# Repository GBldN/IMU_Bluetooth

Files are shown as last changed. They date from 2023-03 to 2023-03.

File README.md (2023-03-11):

# IMU_Bluetooth
<p align="center">
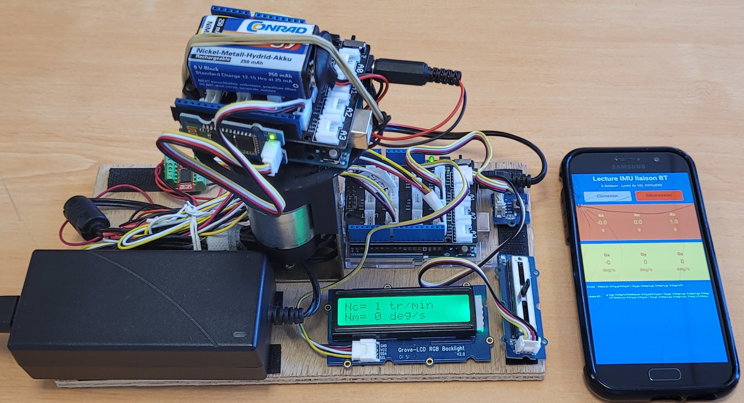
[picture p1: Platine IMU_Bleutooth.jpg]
Moteur à l'arret

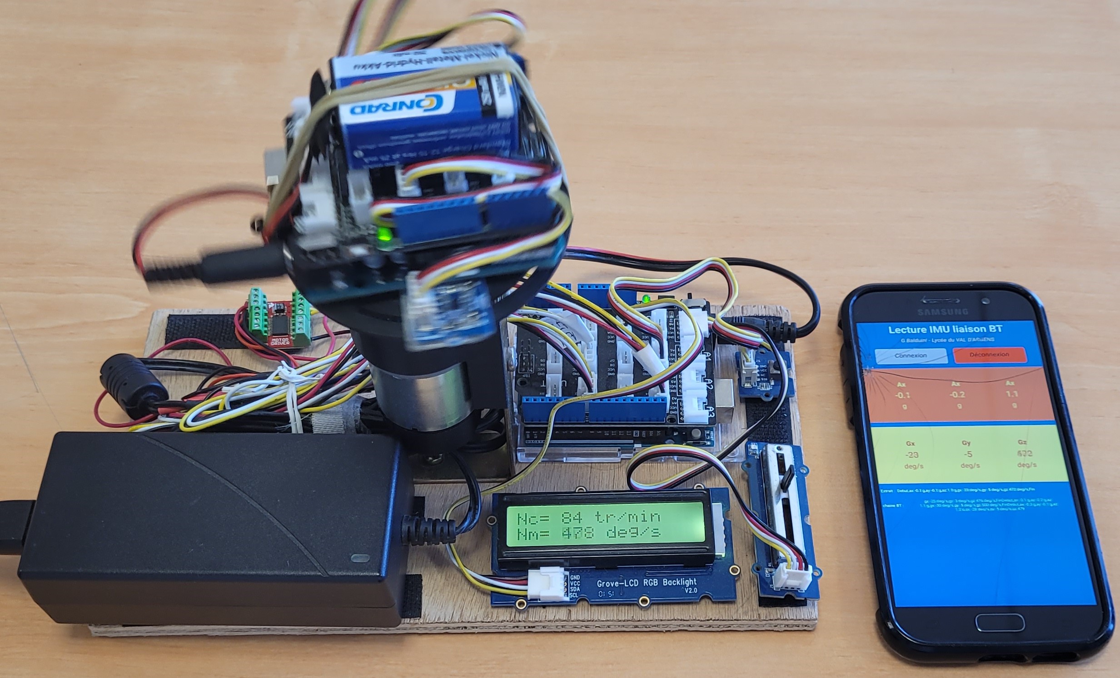
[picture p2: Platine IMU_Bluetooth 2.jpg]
Moteur en rotation
 
</p>

## Présentation

Platine expérimentale pour afficher, en temps réel, les données lues par une centrale inertielle incluant un accéléromètre et un gyromètre.
Il est possible de piloter la fréquence avec un potentiomètre linéaire.
L'écran LCD permet d'afficher la fréquence de consigne (en tr/min) et la mesure de la vitesse angulaire en °/s.
Les données de la centrale sont envoyées en Bluetooth vers un smartphone et une application spécifique.

Une vidéo du programme en situation est disponible  [youtu.be/u4rxh-nPM8k](https://youtu.be/_Ql979rKE8E)

## Matériel utilisé
### Centrale inertielle :
- Un Arduino UNO
- Une centrale inertielle Grove_IMU_6 DOF : [wiki.seeedstudio.com/Grove-6-Axis_AccelerometerAndGyroscope](https://wiki.seeedstudio.com/Grove-6-Axis_AccelerometerAndGyroscope/) 
- Un module Bluetooth Grove - Serial Bluetooth v3.0 [wiki.seeedstudio.com/Grove-Serial_Bluetooth_v3.0](https://wiki.seeedstudio.com/Grove-Serial_Bluetooth_v3.0/)
- Une pile 9V pour l'alimentation

### Banc moteur
- Un Arduino UNO
- Un écran LCD RGB BLACKLIGHT : [wiki.seeedstudio.com/Grove-LCD_RGB_Backlight](https://wiki.seeedstudio.com/Grove-LCD_RGB_Backlight/)
- Un potentiomètre linéaire Grove Slide Potentiometer : [wiki.seeedstudio.com/Grove-Slide_Potentiometer](https://wiki.seeedstudio.com/Grove-Slide_Potentiometer/)
- Un Driver moteur Sparkfun TB6612FNG : [sparkfun.com/tutorials/tb6612fng-hookup-guide](https://learn.sparkfun.com/tutorials/tb6612fng-hookup-guide?_ga=2.155362748.600943259.1678452372-1239022160.1678452372)
- Un moto réducteur POLOLU #4753 avec une réduction de 50:1 et 64CPR (rise and fall) : [pololu.com/product/4753](https://www.pololu.com/product/4753)
- Une équerre de renfort Zingué 100x100x22mm
- Une interface de fixation du motoréducteur sur l'équerre, imprimée en 3D (voir fichier stl)
- Un plateau à fixer sur la sortie du motoréducteur imprimé en 3D (voir fichier stl)
- Une alimentation CC 12V 3A ou plus

### Application Android
L'application permet d'afficher en temps réel :
- les 3 valeurs Ax, Ay et Az de l'accéléromètre
- Les 3 valeurs Gx, Gy et Gz du gyromètre

L'Arduino envoie, par la liaison bluetooth, une chaine de caractères :  
"Debut,ax:±##.##;g,ay:±##.##;g,ay:±##.##;g,gx:±####;deg/s,gy:±####;deg/s,gz:±####;deg/s,Fin  "  
Dont les ### sont les valeurs de chaque composante.

L'application a été développé avec APP INVENTOR :  [appinventor.mit.edu/](https://gallery.appinventor.mit.edu/?galleryid=7bed003b-4152-40f3-b9e8-77ac0583e04f)
Le fichier apk est fourni dans les fichiers

### Explications :
Le principe est le suivant :
- Le µC de la centrale envoie en permanence les 6 composantes d’accélérations et de vitesses angulaires en temps réel par l’intermédiaire du Bluetooth
- Le smartphone affiche les 6 valeurs.
- On peut contrôler « précisément » la fréquence de rotation du motoréducteur et lire sur la platine la valeur « réelle » en °/S
- Il est donc possible de vérifier les valeurs mesurées par le gyromètre en °/S et éventuellement celle de l’accéléromètre (accélération centripète) a= ω²∙ Rayon

Pour tout renseignement complémentaire [gael.balduini@gmail.com](mailto:gael.balduini@gmail.com)

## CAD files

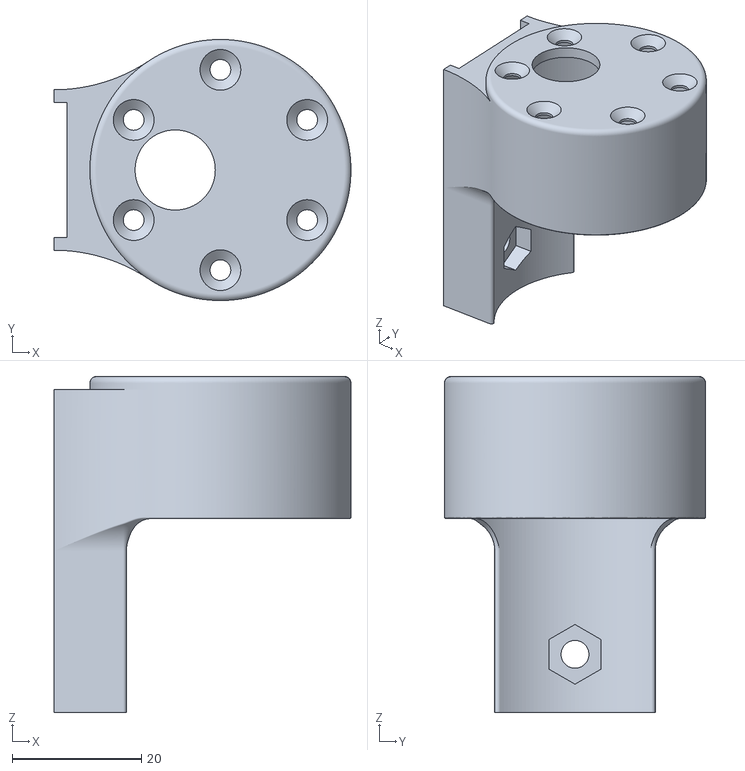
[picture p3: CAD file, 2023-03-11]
Support Moteur Pololu 37D.STL
46.0 x 40.4 x 52.0

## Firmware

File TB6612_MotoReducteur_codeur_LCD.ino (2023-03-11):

/* ################# PROGRAMME DE PILOTAGE D'UN MOTOREDUCTEUR AVEC LE DRIVER TB6612FNG  #################
 * Programme pour piloter en vitesse un moto réducteur à partir d'un signal PWM et mesurer la fréquence de rotation avec son codeur.
 * 
 * Le mini driver moteur utilisé est un Sparkfun TB6612FNG https://www.sparkfun.com/products/14451 qui permet de controler 2 moteurs CC jusqu'à 1,2A par canal
 * Le moteur utilisé est un POLOLU #4753 avec une réduction de 50:1 et 64CPR (rise and fall)  https://www.pololu.com/product/4753
 * Son codeur doit être connecté aux 2 entrées d'interruption INT0 sur D2 et INT1 sur D3.
 * Mais il est possible d'adapter le programme à n'importe quel moteur et codeur.
 * 
 * Ce programme permet :
 *  - De controler la variation de vitesse ainsi que le sens de rotation par un potentiomètre (arrêt en position médiane) 
 *  - De Mesurer les 2 impulsions du codeur grâce à la lecture des interruptions
 *  - De calculer la fréquence de rotation DE LA SORTIE DU REDUCTEUR en tenant compte CPR (nombre d'implusions par tour) ainsi que le rapport de réduction du réducteur
 *  - D'afficher la valeur de Fréquence de consigne et de fréquence mesuré sur un écran LCD
 *  
 * Le calcul à intervalle régulier est géré par le TIMER2 controlé par les registres
 *  
 * Un exemple d'application est disponible sur le github https://github.com/GBldN/IMU_Bluetooth
 * 
 * Une vidéo du programme en situation est disponible sur youtube https://youtu.be/u4rxh-nPM8k
 *  
 * version=1.0
 * author=gael.balduini@gmail.com
 * licence=CC-by-nc-sa
 * maintainer=Arduino <info@arduino.cc>
 * category=Data Processing
 */

/* ##### PARAMETRES POUR PERSONNALISER LE MATERIEL ##### */
  #define f_ech             50                //Choix d'une fréquence en Hz pour le calcul à intervalle régulier
  #define prediviseur       64                //Prédiviseur du timer 2 pour un réglage de l'interruption à 976,5625 Hz
  #define TCNT_init         6                 //Choix d'une valeur de départ du comptage pour régler une fréquence de 1000 Hz
  #define f_timer()         (16000000 / prediviseur / ( 256 - TCNT_init))   //Calcul de la fréquence d'interruption
  
  #define CPRtick           64                //Nombre de ticks par tour du codeur (fonction du codeur utilisé)
  #define reduction         50                //Rapport de réduction du réducteur entre le codeur et l'arbre de sortie
  #define N_max             220               //Fréquence de rotation maxi de l'arbre de sortie ( ± en tr/min)
  #define Offset            10                 //Offset +/- pour l'arrêt du piltage de l'arbre de sortie (en tr/min) nécessaire pour la stabilité à l'arrêt
 
/* ##### DEFINITION DES CONNEXIONS ##### */
  #define An0_Pin           A0                //Port de connexion de l'entrée du CAN An0
  #define Bp1Pin            8                 //Port de connexion de l'entrée du bouton poussoir de calibrage (en option)

  #define MotSTBYPin        4                 //Port de connexion du signal STANDBY du driver de puissance
  #define MotPWMAPin        5                 //Port de connexion du signal PWMA du driver de puissance
  #define MotAIN1Pin        6                 //Port de connexion du signal AIN1 du driver de puissance
  #define MotAIN2Pin        7                 //Port de connexion du signal BIN1 du driver de puissance



/* ##### DEFINITION DES BIBLIOTHEQUES ET DES VARIABLES ##### */
/* -- Intégrations des bibiothèques -- */
 #include <Wire.h>                            //Intégration de la bibliothèque "wire" pour la gestion de l'I2C
 #include "rgb_lcd.h"                         //Intégration de la biblitothèque "rgb_lcd" pour la commande de l'écran GROVE I2C
 rgb_lcd lcd;                                 //Création de la fonction nommée ici "lcd"

/* -- Définition des variables pour l'état TOR ou les valeurs numériques des entrées -- */
  uint16_t           An0            = 0;      //Variable pour la position du potentiomètre de réglage de la consigne de 0 à 1024 (CAN 10 bits)
  bool               etat_BP        = false;  //Variable pour connaitre l'état du bouton poussoir
  volatile int32_t   tics            = 0;      //Variable pour le nombre de tics du capteur
  int32_t            tics_precedent  = 0;      //Variable pour le calcul de la fréquence
  uint32_t           t0             = 0 ;     //Variable pour le calcul du temps

  /* -- Définition des variables pour le pilotage -- */
  float              N_consigne     = 0;      //Variable pour la consigne de fréquence de rotation en tr/min
  float              N_mesure       = 0;      //Variable pour la fréquence réelle mesurée en tr/min
  float              erreur         = 0;      //Variable pour la mémorisation de la vitesse
  int16_t            MLI_mot        = 0;      //Variable pour le réglage du rapport cyclique du moteur

/* -- Déclaration des fonctions utiles au programme -- */
  uint8_t            compteur       = 0;      //Compteur pour le régalge de l'opération à lancer à la fréquence choisie
  uint8_t            CouleurR       = 0;      //Variable pour la gestion de la couleur Rouge de l'écran LCD
  uint8_t            CouleurV       = 255;    //Variable pour la gestion de la couleur Verte de l'écran LCD
  uint8_t            CouleurB       = 0;      //Variable pour la gestion de la couleur Bleu de l'écran LCD


  
/**************************************************************
      ROUTINE D'INITIALISATION  (exécutée une seule fois)
 **************************************************************/
void setup()
{
/* -- Configuration des broches en ENTREE ou SORTIE -- */
  pinMode(An0_Pin,          INPUT);
  pinMode(Bp1Pin,           INPUT);
  pinMode(MotAIN1Pin,       OUTPUT);
  pinMode(MotAIN2Pin,       OUTPUT);
  pinMode(MotPWMAPin,       OUTPUT);
  pinMode(MotSTBYPin,       OUTPUT);

  pinMode(2,       INPUT_PULLUP);
  pinMode(3,       INPUT_PULLUP);

  TWBR = ((F_CPU / 400000L) - 16) / 2;          //Réglage de la fréquence de fonctionnement du bus I2C à 400kHz
  setup_timer2();                               //Appel de la routine de configuration du timer 2
  


/* -- configuration des fonctions spéciales nécessaires au programme */
  Serial.begin(115200);                       //Initialisation de la bibliothèque Moniteur série
  lcd.begin(16, 2);                             //Démarrage et configuration de la fonction LCD pour un écran 2 lignes 16 caractères
  lcd.clear();                                  //Effacement de l'écran
  lcd.setRGB(0, 255, 0);                        //Réglage de la couleur de l'écran en VERT
  lcd.setCursor(0, 0);                          //Positionnement du curseur (caractère,ligne)
  lcd.print("PILOTAGE VITESSE");                //Ecriture du titre du programme sur le LCD
  lcd.setCursor(0, 1);
  lcd.print(" CODEUR ROTATION");                //Explication du role du bouton d'initialisation
  delay(2000);                                  //Pause pour l'affichage du nom du programme
  lcd.clear();

  attachInterrupt(digitalPinToInterrupt(2), Comptage, CHANGE);  //Création de l'interruption sur la broche INT0 : D2
  attachInterrupt(digitalPinToInterrupt(3), Comptage2,CHANGE);  //Création de l'interruption sur la broche INT1 : D3                                
  
  digitalWrite(MotSTBYPin,HIGH);                //mise à 1 du signal STANDBY du driver pour son activation
  t0 = millis();
}

/**************************************************************
           BOUCLE PRINCIPALE (exécutée en permanence)
 **************************************************************/
void loop()
{ 
/* -- Lecture des valeurs de entrées -- */
  An0  = analogRead(An0_Pin);                   //Lecture de la valeur du CAN de l'entrée A0
  N_consigne = map(An0,0,1023,-N_max,N_max);    //Définition de la valeur ± de fréquence de consigne en tr/min
 
/* -- Arret du moteur en cas d'appui sur le bouton poussoir -- */
 /* if ( digitalRead(Bp1Pin) == HIGH && etat_BP == false )
  {
    digitalWrite(MotSTBYPin,LOW);                //mise à 0 du signal STANDBY du driver pour son activation
    etat_BP = true;
  }
  
  if ( digitalRead(Bp1Pin) == LOW )
  {
    digitalWrite(MotSTBYPin,HIGH);                //mise à 1 du signal STANDBY du driver pour son activation
    etat_BP = false;
  }
*/
/* -- Affichage sur le moniteur série -- */
  Serial.print("N_consigne= " + String(N_consigne) + " tr/min ; N_mesure = " + String(N_mesure) + " tr/min"  );
  Serial.print(" | Pilotage moteur : " + String(MLI_mot));  Serial.print(" | tics = " + String(tics));
  Serial.println();

 PILOTAGE_MOTEUR();                             //Appel de la routine de pilotage du moteur

/* -- Gestion de la couleur de l'écran en fonction de la valeur du CAN  -- */
  
/* -- Affichage des valeurs sur l'écran tous les 200 ms-- */
  if ( ( millis() - t0 ) > 400 )
  {
    if ( abs(N_mesure) <= Offset )                      //Si la valeur du CAN est médiane (512) l'écran est VERT
    {
      CouleurB = 0 ;
      CouleurV = 255;
      CouleurR = 0;
    }
    if ( N_mesure < -Offset  )                //Si la valeur est dans la moitié inférieure l'écran tend vers le BLEU
    {
      CouleurB = (N_max - float(N_mesure)) * 255 / N_max;
      CouleurV = 255 * float(N_mesure) / N_max;
      CouleurR = 0;
    }
    if ( N_mesure > Offset )                  //Si la valeur est dans la moitié supérieure l'écran tend vers le ROUGE
    {
      CouleurB = 0;
      CouleurV = 255 * ( N_max - float(N_mesure)) / N_max;
      CouleurR = 255 * ( float(N_mesure) - N_max) / N_max;
    }
  
    lcd.setRGB(CouleurR, CouleurV, CouleurB); //Définition de la couleur de l'écran en fonction des valeurs
    lcd.clear();                              //Effacer l'écran
    lcd.setCursor(0, 0);                      //Ecriture sur la première ligne
    lcd.print("Nc= ");
    lcd.print(N_consigne,0);
    lcd.print(" tr/min");
    lcd.setCursor(0, 1);                      //Ecriture sur la seconde ligne, 2ème caractère
    lcd.print("Nm= "); lcd.print(N_mesure*6,0); lcd.print(" deg/s");
    //lcd.print("Nm= "); lcd.print(N_mesure,0); lcd.print(" tr/min");
    //lcd.print("tics");   lcd.print(tics);
    t0 = millis();
  }


}


/***********************************************************************
 *         ROUTINE EXECUTEE A CHAQUE PERIODE DEFINIE PAR LA FREQUENCE  *
 *            Insérer ici les calculs à faire à fréquence régulière    *
 ***********************************************************************/
void calcul()
{
 N_mesure = float( tics - tics_precedent) * f_ech * 60 / CPRtick / reduction;  //Calcul de la fréquence de rotation réelle de l'arbre de sortie en Hz
 tics_precedent = tics;                                                     //Mémorisation du nombre de tics pour le calcul suivant
   
 //erreur = N_consigne - N_mesure;                                            //Calcul de l'erreur
      /* -- Calcul de la commande MLI moteur -- */
 MLI_mot = map(N_consigne,-N_max,N_max,255,-255);
 //MLI_mot = Kp * erreur + Ki * somme_erreur + Kd * delta_erreur;           //Calcul de la valeur de pilotage asservie par correction PID ATTENTION MANQUE LES VARIABLES Somme et delta erreur)
 
      /* -- Normalisation et contrôle de dépassement du pilotage (si asservissement) -- */
 //if (MLI_mot >  255) MLI_mot =  255;             //Limitation du pilotage à la valeur mini admissible
 //if (MLI_mot < -255) MLI_mot = -255;             //Limitation du pilotage à la valeur mini admissible

}
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

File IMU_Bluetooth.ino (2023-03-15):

/* ################# PROGRAMME POUR ENVOYER EN BLUETOOTH LES VALEURS D'UNE CENTRALE INERTIELLE #################
 * 
 * Ce programme permet d'envoyer en Bluetooth les valeurs d'accélérations et de vitesses angulaires lues grâce à la centrale inertielle 
 *   - La centrale utilisée est une Grove_IMU_6 DOF : https://wiki.seeedstudio.com/Grove-6-Axis_AccelerometerAndGyroscope/ 
 *   - Le module Bluetooth utilisé est un module Grove - Serial Bluetooth v3.0 https://wiki.seeedstudio.com/Grove-Serial_Bluetooth_v3.0/
 * 
 * Pour simplifier le décodage le programme envoie en BT une trame de caractères ASCII : "Debut,ax:±##.##;g,ay:±##.##;g,ay:±##.##;g,gx:±####;deg/s,gy:±####;deg/s,gz:±####;deg/s,Fin  "
 *            dont les #### correspondent aux valeurs
 *  
 * La réception des informations est prévue avec un smartphone. L'application Android développé avec APP INVENTOR https://gallery.appinventor.mit.edu/?galleryid=7bed003b-4152-40f3-b9e8-77ac0583e04f
 * 
 * L'ensemble des descriptions et ressources sont disponibles sur le github https://github.com/GBldN/IMU_Bluetooth
 * 
 * Une vidéo du programme en situation est disponible https://youtu.be/u4rxh-nPM8k
 *  
 * version=1.0
 * author=gael.balduini@gmail.com
 * licence=CC-by-nc-sa
 * maintainer=Arduino <info@arduino.cc>
 * url=https://github.com/GBldN/IMU_Bluetooth
 */

/* ##### DECLARATION DES MACROS ##### */
   
/* ##### DECLARATION DES CONSTANTES ##### */
  #define BtTxPin                   4             //Port de connexion Tx-O du module BT
  #define BtRxPin                   5             //Port de connexion Rx-I du module BT
  
  #define       f_ech               100           //Choix d'une fréquence en Hz pour le calcul à intervalle régulier entre 1 et 500 Hz (ATTENTION ! 1000 doit être un multiple de f_ech)
  
  #define       pleine_echelle_acc  16            //réglage de la gamme de mesure de l'accéléromètre ±2g ; ±4g ; ±8g ou ±16g
  #define       sensi_acc           488;          //Sensibilité de l'accéléromètre en g/LSB   (réglé par défault pour 4g mais se personnalise en fonction de la pleine échelle
  #define       pleine_echelle_gyr  2000          //réglage de la gamme de mesure du gyromètre ± 250; 500; 1000; 2000 °/s (2; 41; 42; 83; 167; 333 tr/min) ou ±125°/s pour le LM6DS3 
  #define       sensi_gyr           70000;        //Sensibilité du gyromètre       en dps/LSB (réglé par défault pour 2000 °/s mais se personnalise en fonction de la pleine échelle)
  

/* ##### DEFINITION DES BIBLIOTHEQUES ET DES VARIABLES ##### */
/* -- Intégrations des bibiothèques -- */
  #include <SoftwareSerial.h>                     //Emulateur d'une liaison série pour l'utilisation sur d'autres broches que les 0 et 1
  #include <Wire.h>                               //Intégration de la bibliothèque "wire" pour la gestion de l'I2C

/* -- Définition des variables pour l'état TOR ou les valeurs numériques des entrées -- */
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
